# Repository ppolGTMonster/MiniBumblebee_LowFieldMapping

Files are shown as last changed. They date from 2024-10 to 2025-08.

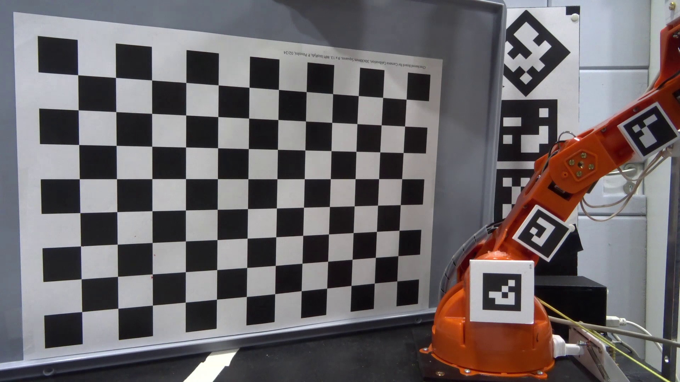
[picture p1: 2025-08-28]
4_MotionTracking/42_Software/0_calibration/calibration_result/img_calibration/image_19.jpg

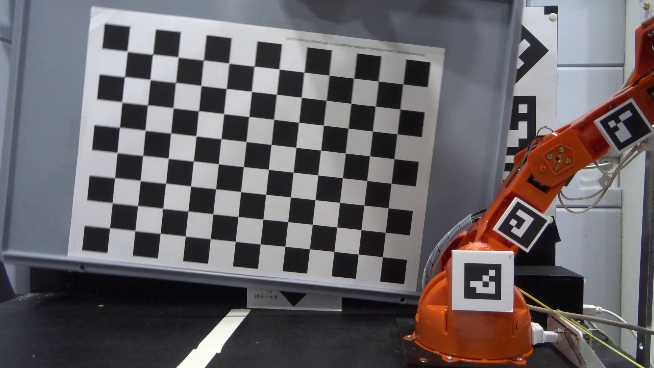
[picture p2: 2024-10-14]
4_MotionTracking/42_Software/0_calibration/calibration_result/img_calibration/image_8.jpg

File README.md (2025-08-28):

# Easy Scalable, Low-Cost Open Source Magnetic Field Detection System for Evaluating Low-Field MRI Magnets using a Motion Tracked Robot

## Author:
Pavel Povolni <pavel.povolni@tuebingen.mpg.de>

## Other Contributors to this hard- and software:
Felix Glang
  *  https://github.com/fglang
  * helped with the optimizers to design the hardware (fmincon & genetic)

Praveen Valsala
  * https://github.com/praveenivp
  * helped with reconstruction of MRI Data

Florian Birk
  * https://github.com/birkfl
  * helped with the Motion Tracking & the openCV Library

Sergej Maltsev
  * https://github.com/TheWinterProgrammer
  * helped with the Hardware 

## How to use

We tried our best to make the hardware as reproducible as possible and to develop the software without expensive extra toolboxes in Matlab (data evaluation), Python (motion tracking) and C++ (embedded code).
The PCBs were designed in KiCad 7 (free).
The mechanical components were designed with Autodesk Inventor 2021, although the Step files can be opened in any other CAD tool.

To get you started with the project as easily as possible, there are 4 instruction pdf's:
* Hallsensor (description of hardware & software for the hall sensor and calibration)
* Robot (description of the hardware & software for the robot used, including control)
* Motion tracking (description of the motion tracking setup & camera, including calibration)
* Mapping (description of the measurement process)

## Name
We always refer to this robot as Mini-Bumblebee in our team. The “big” Bumblebee refers to the large cubic robot that was built. Bumblebee itself stands for:
* B-Field
* Unterstanding and
* Mapping using
* Benchmarked
* Localized Hall
* Effect-based 
* Background
* Estimation and
* Evaluation

## Citing

If you use this code, please cite the corresponding paper:

Povolni, P., Bendfeld, R., Maltsev, S. et al. Easy scalable, low-cost open-source magnetic field detection system for evaluating low-field MRI magnets using a motion-tracked robot. Magn Reson Mater Phy (2025). https://doi.org/10.1007/s10334-025-01239-1

https://link.springer.com/article/10.1007/s10334-025-01239-1

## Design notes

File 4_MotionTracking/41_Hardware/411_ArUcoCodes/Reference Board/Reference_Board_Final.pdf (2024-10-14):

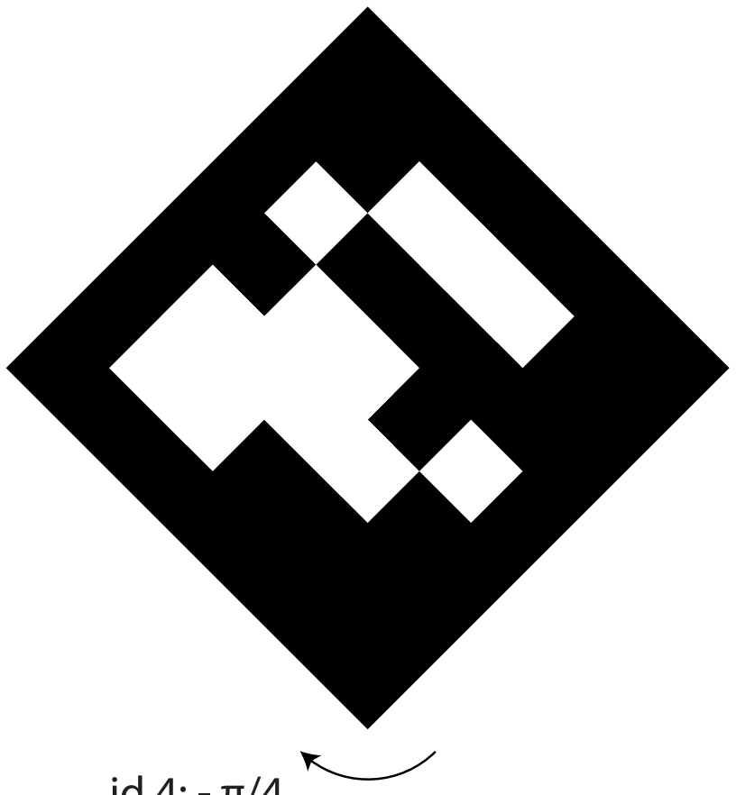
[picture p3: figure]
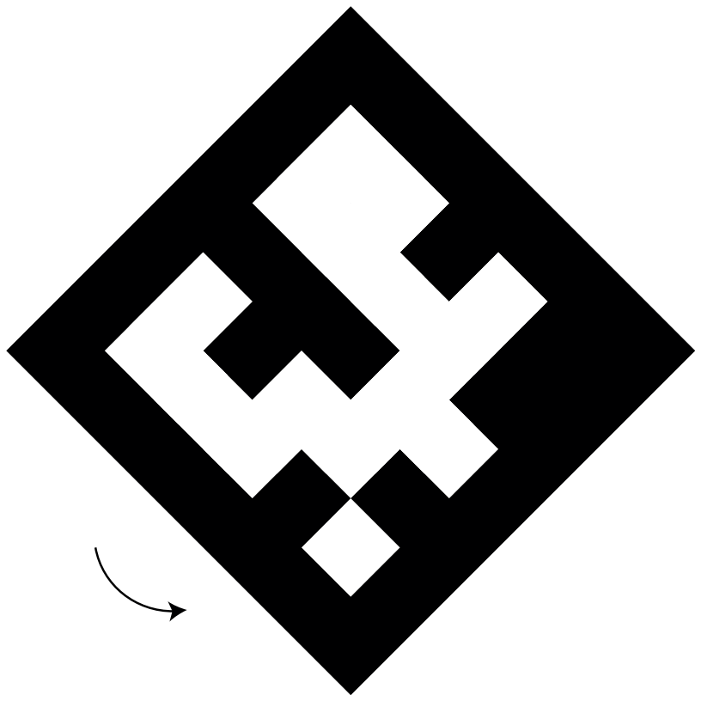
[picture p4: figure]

id 5 | id 4: - π/4 | id 3 | id 2: + π/4

id 1

id 0

# ArUco 5x5, 80x80mm

# Origin Reference Board

(0|0|0)

Translation to Magnet FOV Center: | (-181.5 |-186 | |200) mm
Translation to Robot Base Center: | (340-d |-108 | |200) mm

### d: Distance between edge of reference board and robot base holder (square with side length 130mm)

y

x
z

O RB

ID | x | y | z | Rotation
0 | 340 | 40 | 0 | 0
1 | 340 | 130 | 0 | 0
2 | 340 | 230 | 0 | + π/4
3 | 240 | 230 | 0 | 0
4 | 140 | 230 | 0 | - π/4
5 | 40 | 230 | 0 | 0
6 | 60 | -48 | 60 | + π/4

Position ArUco Center, Size ArUco: 5x5, 80mm id6: Positioned on extra 3d-printed holder
MPI bioKyb, P. Povolni, 02/24

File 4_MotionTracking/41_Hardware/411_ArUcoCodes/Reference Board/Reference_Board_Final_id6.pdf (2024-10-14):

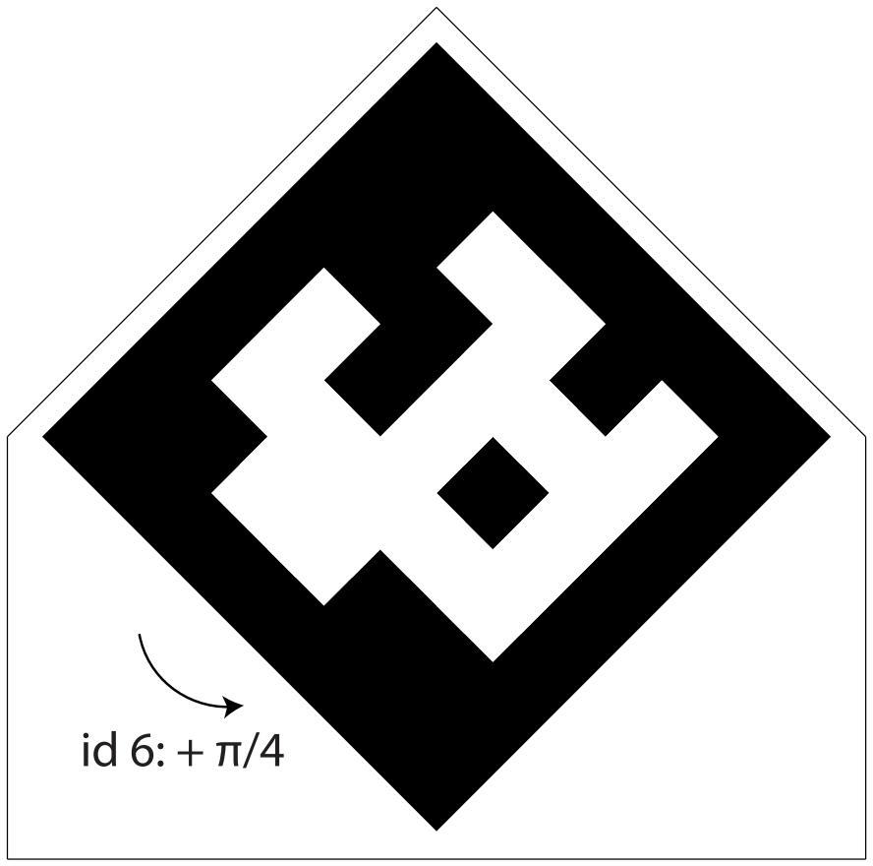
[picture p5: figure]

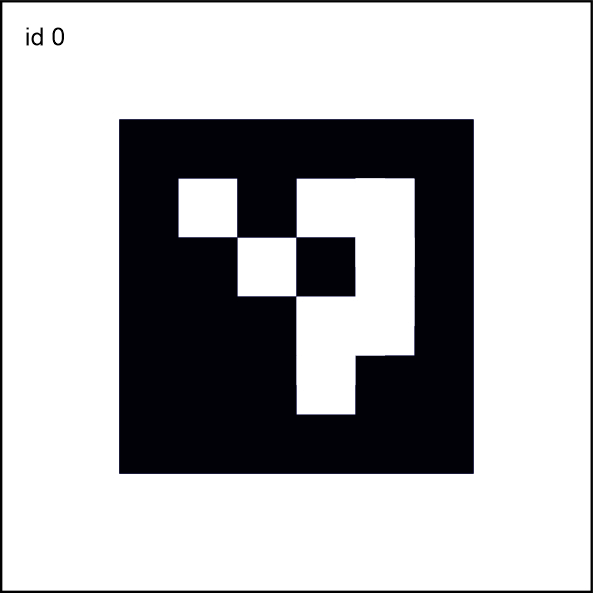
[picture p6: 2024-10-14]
3_5DoF_Robot/31_Hardware/311_RobotCAD_AutodeskInventor/2_Aruco_Marker/Marker_Robot_id0.jpg

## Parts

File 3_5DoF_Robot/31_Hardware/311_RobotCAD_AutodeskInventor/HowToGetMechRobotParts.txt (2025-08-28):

In this project, we used the TinkerCAD Braccio robot from Arduino.
CAD is not absolutely necessary. 
In our case, the robot's CAD was used to position the markers correctly and measure the lengths and positions. 

You can download the CAD for the Arduino robot directly:
https://content.arduino.cc/assets/braccio%20cad.zip

We used the CAD from GeekThomad from the GrabCAD platform:
https://grabcad.com/library/arduino-braccio-robotic-arm-1/details?folder_id=13655787
Published: April 21, 2023
(Check License: https://grabcad.com/terms, commercial use is prohibited)
This CAD is much better structured and much easier to use. Take a look and see what you need and which you can use.

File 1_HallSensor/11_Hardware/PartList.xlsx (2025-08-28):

Order list for electronic components
ID | Part-Info | Manufacturer | Part# Manufacturer | Part# Mouser | Amount | Comment
A1 | µC ESP32 Seeed XIAO Module | Seeed Studio | 113991054 | 713-113991054 | 1
C2,C4,C13,C6,C10,C26,C7,C25,C16,C20,C19,C24,C17,C22,C9,C14,C15,C12,C27,C28,C8,C21,C11,C5,C18,C23 | C 100nF | Wurth Elektronik | 885012206095 | 710-885012206095 | 26 | could be any cheaper option
C33,C34,C29,C30,C32,C35,C1,C36,C31,C3 | C 10uF | Wurth Elektronik | 885012106006 | 710-885012106006 | 10 | could be any cheaper option
J1 | Connector Hallsensor PCB (Male) | Phoenix Contact | 1844249 | 651-1844249 | 1 | could be any cheaper option. No big deal regarding shielding or similar
J1-2 | Connector Hallsensor Wire (Female) | Phoenix Contact | 1840395 | 651-1840395 | 1 | could be any cheaper option. No big deal regarding shielding or similar
J3 | Connector Power PCB (Male) | Phoenix Contact | 1844210 | 651-1844210 | 1 | not necessary (USB C has enough power)
J3-2 | Connector Power Wire (Female) | Phoenix Contact | 1840366 | 651-1840366 | 1 | not necessary (USB C has enough power)
H7,H2,H4,H5,H6,H1,H8,H3 | Hallsensor +-100mT Type | Allegro MicroSystems | ALS31300EEJASR-1000 | 250-31300EEJASR1000 | 8
H7,H2,H4,H5,H6,H1,H8,H3 | Hallsensor +-50mT Type | Allegro MicroSystems | ALS31300EEJASR-500 | 250-31300EEJASR500 | 8
D10,D13,D2,D15,D3,D5,D12,D1,D14,D9,D16,D6,D11,D7,D4,D8 | LED red, Low Power | ams OSRAM | LS L29K-G1J2-1 | 720-LSL29K-G1J2-1-Z | 18
 | R 0Ohm | Vishay / Dale | RCS06030000Z0EC | 71-RCS06030000Z0EC | 18
R1,R63,R65,R66,R44,R67,R61,R64,R62 | R 10kOhm | YAGEO | AC0603JR-0710KL | 603-AC0603JR-0710KL | 9
R17,R28,R15,R43,R30,R19 | R 11.5kOhm | Bourns | CR0603-FX-1152ELF | 652-CR0603FX-1152ELF | 16
R52,R9,R48,R56,R3,R46,R50,R54,R60,R6,R2,R8,R58,R10,R4,R5 | R 147 Ohm | YAGEO | RC0603FR-13147RL | 603-RC0603FR-13147RL | 16
R42,R16,R29,R18,R31 | R 23.2kOhm | Bourns | CR0603-FX-2322ELF | 652-CR0603FX-2322ELF | 16
R7 R2 | R 2kOhm | YAGEO | AC0603FR-072KL | 603-AC0603FR-072KL | 2
R46, R61, R50, R52, R54, R56, R58, R60 | R 820 Ohm | TE Connectivity / Holsworthy | CRGCQ0603F820R | 279-CRGCQ0603F820R | 8
SW1 | Reset Push-Button | CUI Devices | TS04-66-73-BK-260-SMT | 179-TS046673BK260SMT | 1 | not necessary (Power Cycle does the same)
Mechanical Parts (Self Print etc)
Name | File Location | How to manifacture | Amount
Base_Protection | 112_CAD Files\Base | * 3D Print or * Laser Cutting or * manual (sawing/drilling) | 2
Hallsensor_DistanceBolt_8mm4 | 112_CAD Files\SensorHead | * 3D Print (PETG) | 3
Small Parts
Name | Amount
M3 15mm Plastic Screws with washer/nut | 3
Cable tie 2.5mm | 2

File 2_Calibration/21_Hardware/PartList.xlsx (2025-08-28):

Mechanical Parts (Self Print etc)
Name | File Location | How to manifacture | Amount
1) Flange
Mounting_ Ring_ Rear_Part1 | 213_CalibrationSolenoid_CAD_AutodeskInventor\Cylinder | Lasercut (5mm Plexiglas) the best, 3D Print (PETG) also possible | 1
Mounting_ Ring_ Rear_Part2 | 213_CalibrationSolenoid_CAD_AutodeskInventor\Cylinder | Lasercut (5mm Plexiglas) the best, 3D Print (PETG) also possible | 1
Mounting_ Ring_ Rear_thickening | 213_CalibrationSolenoid_CAD_AutodeskInventor\Cylinder | Lasercut (5mm Plexiglas) the best, 3D Print (PETG) also possible | 2
Mounting_Ring_Front | 213_CalibrationSolenoid_CAD_AutodeskInventor\Cylinder | Lasercut (5mm Plexiglas) the best, 3D Print (PETG) also possible | 1
Mounting_Ring_Front_Thickening | 213_CalibrationSolenoid_CAD_AutodeskInventor\Cylinder | Lasercut (5mm Plexiglas) the best, 3D Print (PETG) also possible | 2
2) Foot
Mounting_foot | 213_CalibrationSolenoid_CAD_AutodeskInventor\Cylinder | Propably Lasercut the best, but can be 3D printed too (PETG) | 4
3) Slider
Part 1 (Conn_t15) | 213_CalibrationSolenoid_CAD_AutodeskInventor\Slider | Lasercut (5mm Plexiglas) the best, 3D Print (PETG) also possible | 1
Part 2 (Conn_t60) | 213_CalibrationSolenoid_CAD_AutodeskInventor\Slider | Lasercut (5mm Plexiglas) the best, 3D Print (PETG) also possible | 1
Part 3 (Conn_t80) | 213_CalibrationSolenoid_CAD_AutodeskInventor\Slider | Lasercut (5mm Plexiglas) the best, 3D Print (PETG) also possible | 1
Part 4 (Conn_t25) | 213_CalibrationSolenoid_CAD_AutodeskInventor\Slider | Lasercut (5mm Plexiglas) the best, 3D Print (PETG) also possible | 1
Part 5 (Slider_Front) | 213_CalibrationSolenoid_CAD_AutodeskInventor\Slider | Lasercut (5mm Plexiglas) the best, 3D Print (PETG) also possible | 2
Part 6 (Slider_Angle_Distance_Holder) | 213_CalibrationSolenoid_CAD_AutodeskInventor\Slider | Lasercut (5mm Plexiglas) the best, 3D Print (PETG) also possible | 1
Part 7 (Slider_Angle) | 213_CalibrationSolenoid_CAD_AutodeskInventor\Slider | 3D Print (PETG) | 1
Part 8/9 in 3 diff Styles: * HallSensor_Holder_X-Axis * HallSensor_Holder_Y-Axis * HallSensor_Halterung_Z-Axis | 213_CalibrationSolenoid_CAD_AutodeskInventor\Slider\Hallsensor_Mounting | 3D Print (PETG) | each 1
Mechanical Parts (to Buy)
Name | File Location | Where to buy | Amount
enamelled copper wire, 1.5mm Diameter | 213_CalibrationSolenoid_CAD_AutodeskInventor\Cylinder\Cu_Coil | rs-online.com Nr: 779-0741 | 160m
Outer Cylinder Ostendorf Kunststoffe, No. 223000, KG EM Rohr SN 4 Coex DN/OD 200 x 500 mm | 213_CalibrationSolenoid_CAD_AutodeskInventor\Cylinder\KG_Tube_200mm_500mm.ipt | local building materials supplier (e.g. Hornbach/Bauhaus etc) | 1
Inner Cylinder Ostendorf Kunststoffe, No. 222000, KG EM Rohr SN 4 Coex DN/OD 160 x 500 mm | 213_CalibrationSolenoid_CAD_AutodeskInventor\Cylinder\KG_Tube_160mm_500mm.ipt | local building materials supplier (e.g. Hornbach/Bauhaus etc) | 1
2K Epoxy (any other can be used too) | Loctite EA 9466 | rs-online.com Nr: 244-2026 | as needed
Electronic Parts
Name | Description | Where to buy | Amount
Temperature Sensor | Type K Sensor glued to coil to measure the temperature using a standard Multimeter | rs-online.com Nr: 136-5868 | 1

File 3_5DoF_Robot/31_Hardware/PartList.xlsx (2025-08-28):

Mechanical Parts (Self Print etc)
Name | File Location | How to manifacture | Amount
1) Robot
Robot Basis (wooden Plate), 12mm, 130x130mm, Adapter_Plate_12mm | 311_RobotCAD_AutodeskInventor\4_ownParts | simply saw it | 1
Positioning_Robot (Align TinkerCAD Braccio Robot) | 311_RobotCAD_AutodeskInventor\4_ownParts | 3D Print (PETG) | 1
Halterung_Robot (Lever attached to Robot Base and Potentiometer) | 311_RobotCAD_AutodeskInventor\5_Potentiometer | 3D Print (PETG) | 1
Halterung_Winkel (Mounting PCB with Poti) | 311_RobotCAD_AutodeskInventor\5_Potentiometer | 3D Print (PETG) | 1
Adapter_Wrist | 311_RobotCAD_AutodeskInventor\3_Hallsensor_Holder | 3D Print (PETG) | 1
Adapter_Wrist_Hallsensor_220mm | 311_RobotCAD_AutodeskInventor\3_Hallsensor_Holder | 3D Print (PETG) | 1
2) Environment
Backside Wood, 22mm thick, 750x422mm | 313_EnvironmentCAD_AutodeskInventor | simply saw it | 1
Ground Wood, 22mm thick, 750x350mm | 313_EnvironmentCAD_AutodeskInventor | simply saw it | 1
2) Marker
Aruco_Basis_final_id0 | 311_RobotCAD_AutodeskInventor\2_Aruco_Marker | 3D Print (PETG) | 1
Aruco_Shoulder_final_id1 | 311_RobotCAD_AutodeskInventor\2_Aruco_Marker | 3D Print (PETG) | 1
Aruco_Shoulder_final_id2 | 311_RobotCAD_AutodeskInventor\2_Aruco_Marker | 3D Print (PETG) | 1
Aruco_Wrist_final_id3 | 311_RobotCAD_AutodeskInventor\2_Aruco_Marker | 3D Print (PETG) | 1
3) Electronics
Box_Driver_Bottom | 314_Robot_PowerElectronicDriverBox | 3D Print | 1
Box_Driver_Top | 314_Robot_PowerElectronicDriverBox | 3D Print | 1

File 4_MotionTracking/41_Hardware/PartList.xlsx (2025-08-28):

Mechanical Parts (Self Print etc)
Name | File Location | How to manifacture | Amount
1) Marker Reference
Mounting_ID6 | 413_Mounting_ID6_Reference | 3D Print (PETG) | 1
Mounting_ID6_Support | 413_Mounting_ID6_Reference | 3D Print (PETG) | 1

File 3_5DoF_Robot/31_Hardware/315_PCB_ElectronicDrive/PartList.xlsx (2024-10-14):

Order list for electronic components
ID | Part-Info | Manufacturer | Part# Manufacturer | Part# Mouser | Amount | Comment
A1 | Arduino Uno | Arduino | A000073 | 782-A000073 | 1 | Doesn't need to be original Uno. Any copy will work too (eg from Seeed/Adafruit…)
A1-2/1 | Pin-Header for Shield, 6pin | Preci-dip | 801-87-006-53-001101 | 437-8018700653001101 | 1
A1-2/2 | Pin-Header for Shield, 8pin | Preci-dip | 801-87-008-53-001101 | 437-8018700853001101 | 2
A1-2/3 | Pin-Header for Shield, 10pin | Preci-dip | 801-87-010-53-001101 | 437-8018701053001101 | 1
C11,C10,C8,C9,C12,C7,C18,C22,C19,C17,C23 | C 100n SMD1206 | KEMET | C1206C104M5RACTU | 80-C1206C104M5R | 11
C16,C15,C13 | C 47uF, Radial Elko | Wurth Elektronik | 860080674005 | 710-860080674005 | 6
C25,C21,C4,C6,C3,C1,C2,C5 | C 1uF SMD1206 | KEMET | C1206C105K4RAC | 80-C1206C105K4RAC | 8
D1 | LED 3mm | Wurth Elektronik | 151031VS06000 | 710-151031VS06000 | 3
D2 | Rectifiers 50V 1.5a S2A | onsemi / Fairchild | S2A | 512-S2A | 1
F4,F3,F2, F1 | Resettable Fuses - PPTC 6V 1.1A-HD 40A MAX | Bourns | MF-MSMF110-2 | 652-MF-MSMF110-2 | 4
F7,F6,F5 | Resettable Fuses - PPTC 13.2V .75A-HD 100A MAX | Bourns | MF-MSMF075-2 | 652-MF-MSMF075-2 | 3
J1 | Connector Power PCB (Male) | Phoenix Contact | 1803277 | 651-1803277 | 2
J1-2 | Connector Power Wire (Female) |  | 1803578 | 651-1803578 | 2
J3 | Connector Base PCB (Male) | Phoenix Contact | 1803280 | 651-1803280 | 1
J3/J4-2 | Connector Sensor Wire (Female) | Phoenix Contact | 1803581 | 651-1803581 | 2
J4 | Connector Sensor PCB (Male) | Phoenix Contact | 1803439 | 651-1803439 | 1
M3,M5,M2,M4,M6,M1 | Conenctor Stepper Motors | Molex | 22-27-2031 | 538-22-27-2031 | 6 | This connector fits exactly to the wiring of the robot used (Tinkercad Braccio Arduino).Any other connector with 2.54mm pin width (e.g. pin header) can be used
Q1 | BJT npn BC548A | Diotec Semiconductor | BC548A | 637-BC548A | 1
R1 | R 147Ohm , Precise, E196 | Panasonic | ERA-8AEB1470V | 667-ERA-8AEB1470V | 1
R10 | Relay, 10A, 5V Coil | Amphenol Anytek | AHQSH105LM100G | 523-AHQSH105LM100G | 1
R2 | R 1210 Ohm , Precise, E196 | Panasonic | ERA-8AEB1211V | 667-ERA-8AEB1211V | 1
R4,R3,R5 | R 2370 Ohm , Precise, E196 | Panasonic | ERA-8AEB2371V | 667-ERA-8AEB2371V | 3
R8 | R 1 kOhm | YAGEO | RC1206FR-101KL | 603-RC1206FR-101KL | 1
R9,R7,R6 | R 147 Ohm | KOA Speer | RK73H2BTTD1470F | 660-RK73H2BTTD1470F | 3
RV1 | Sliding potentiometer | Bourns | PTA6043-2015DPB103 | 652-PTA60432015DPB10 | 1
SW1 | Reset Push Button | CUI Devices | TS04-66-73-BK-260-SMT | 179-TS046673BK260SMT | 1
U1 | OpAmp TI LM358 | Texas Instruments | LM358P | 595-LM358P | 1
U2 | Voltage References TL431C | onsemi | TL431CLPRPG | 863-TL431CLPRPG | 1
VR1 | Linear Voltage Regulators 5V 500mA Positive 7805 | onsemi | MC78M05CTG | 863-MC78M05CTG | 1

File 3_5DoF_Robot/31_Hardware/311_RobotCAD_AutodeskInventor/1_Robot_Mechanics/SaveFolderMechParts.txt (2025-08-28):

Mechanical Parts of Robot can be saved here. Depends where you grab them

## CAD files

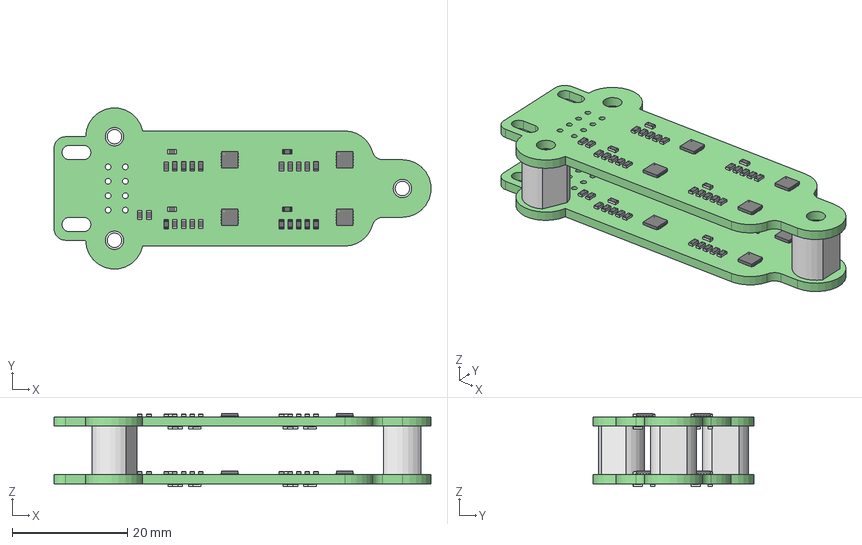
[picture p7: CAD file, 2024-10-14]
1_HallSensor/11_Hardware/112_CAD Files/SensorHead/SensorHead_ASM.stp
65.5 x 28.0 x 12.8 mm
HallSensor_Abstand_8mm4 x 3
Hallmesssonde_Verei x 2

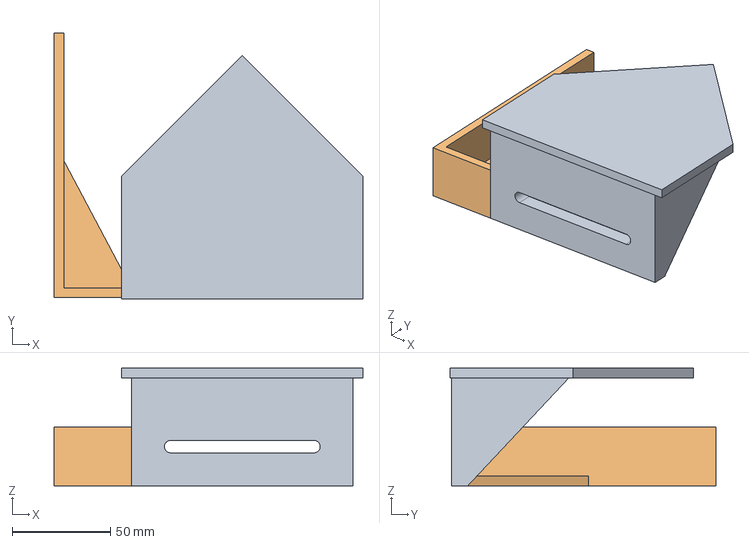
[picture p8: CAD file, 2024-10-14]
4_MotionTracking/41_Hardware/413_Mounting_ID6_Reference/Mounting_ID6_ASM.stp
157.6 x 135.6 x 60.0 mm
Halterung_ID6
Mounting_ID6_Support

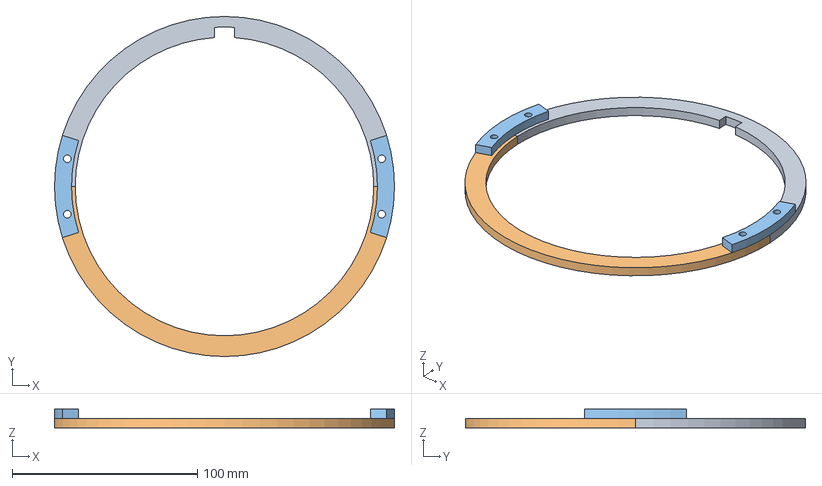
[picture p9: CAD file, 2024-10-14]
2_Calibration/21_Hardware/214_CalibrationSolenoid_CAD_STEP/Cylinder/ASM_Mounting_Ring_Rear.stp
183.6 x 183.6 x 10.0 mm
Montage_Ring_Hinten_Teil1
Montage_Ring_Hinten_Teil1_1
Montage_Ring_Hinten_Aufdickung
Montage_Ring_Hinten_Aufdickung_MIR

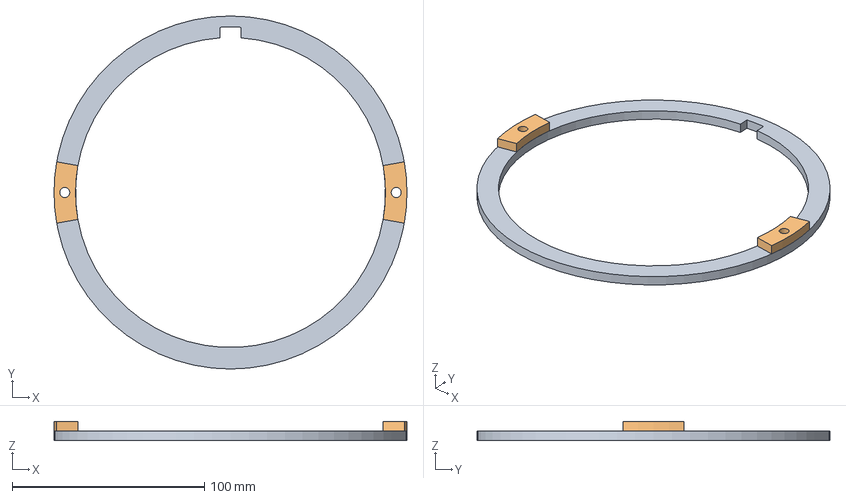
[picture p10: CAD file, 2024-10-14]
2_Calibration/21_Hardware/214_CalibrationSolenoid_CAD_STEP/Cylinder/ASM_Mounting_Ring_Front.stp
183.6 x 183.6 x 10.0 mm
Montage_Ring_Vorne
Montage_Ring_Vorne_Aufdickung_Gewinde
Montage_Ring_Vorne_Aufdickung_Gewinde_MIR

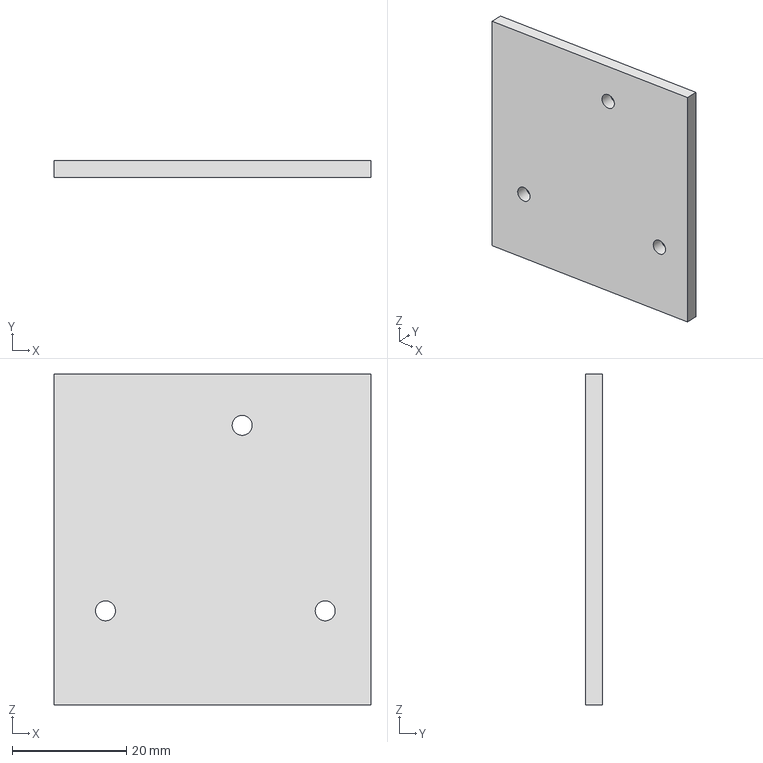
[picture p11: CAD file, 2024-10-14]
1_HallSensor/11_Hardware/112_CAD Files/Base/Base_Protection.stp
55.5 x 3.00 x 58.0 mm

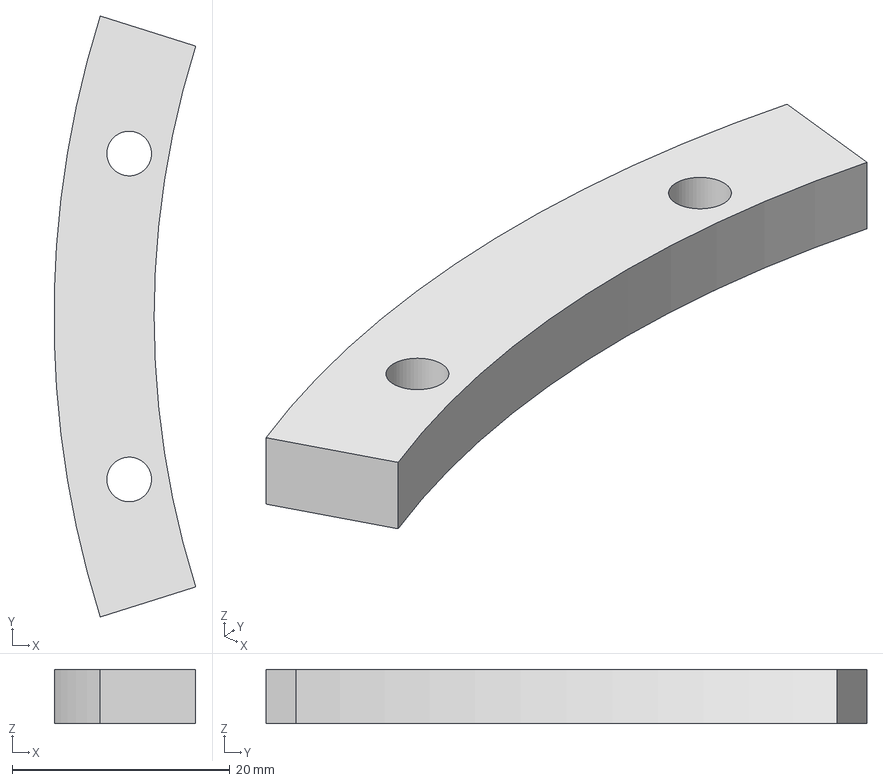
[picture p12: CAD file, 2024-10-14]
2_Calibration/21_Hardware/214_CalibrationSolenoid_CAD_STEP/Cylinder/Mounting_ Ring_ Rear_thickening_MIR.stp
13.0 x 55.2 x 5.00 mm

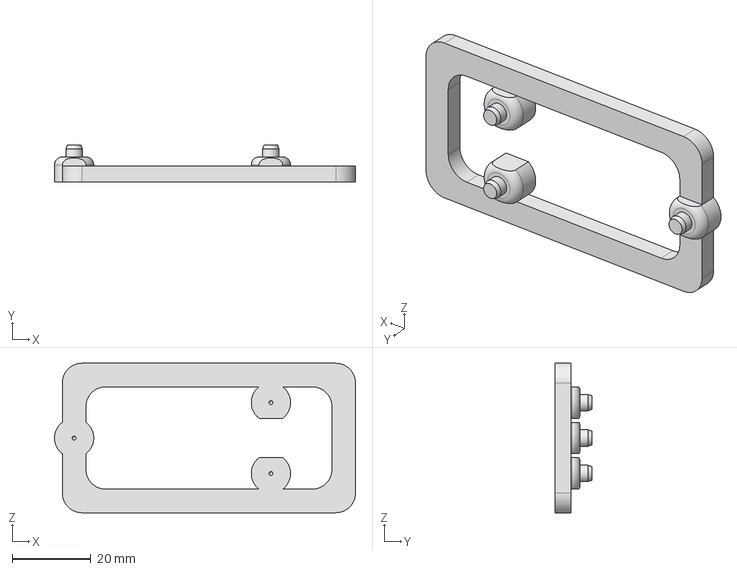
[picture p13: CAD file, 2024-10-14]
2_Calibration/21_Hardware/214_CalibrationSolenoid_CAD_STEP/Slider/Hallsensor_Mounting/Holder_Cal_UpperSensor.stp
76.5 x 9.35 x 38.0 mm

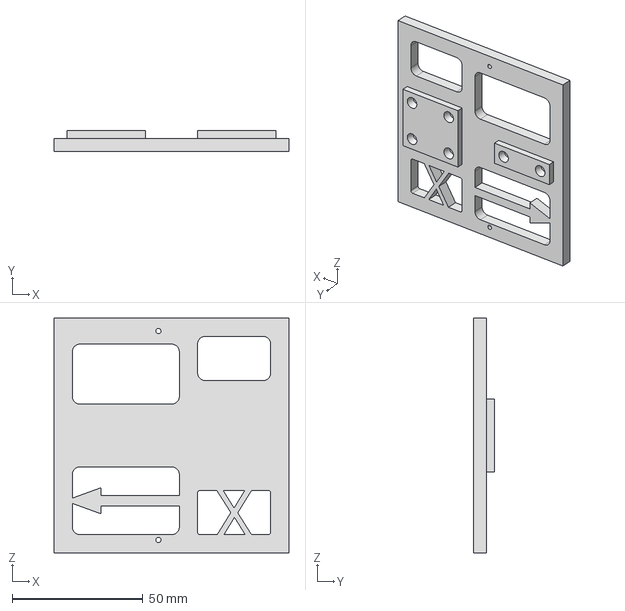
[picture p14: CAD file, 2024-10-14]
2_Calibration/21_Hardware/214_CalibrationSolenoid_CAD_STEP/Slider/Hallsensor_Mounting/X-Axis/HallSensor_Holder_X-Axis.stp
90.0 x 8.00 x 90.0 mm

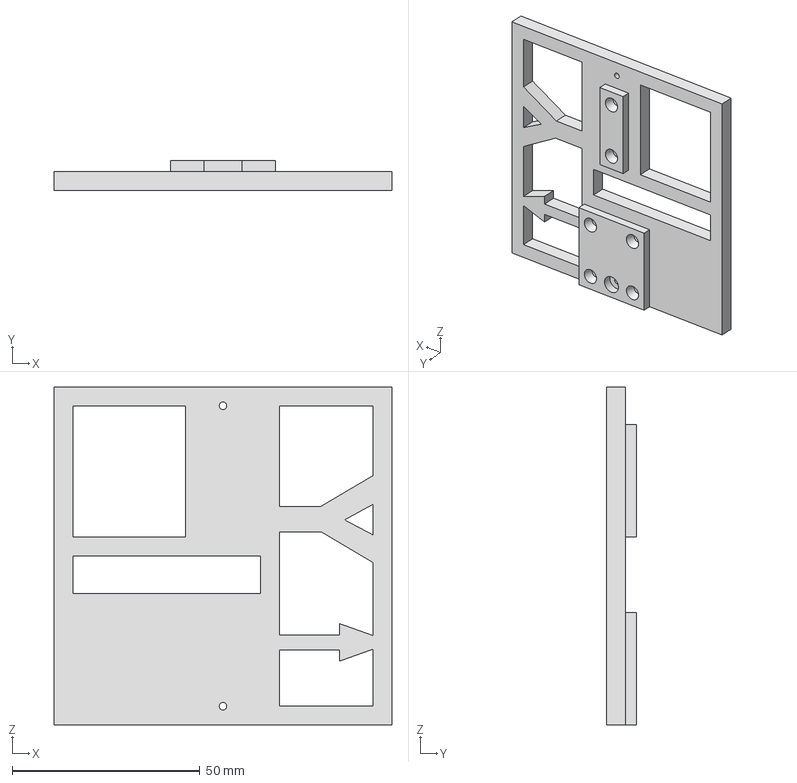
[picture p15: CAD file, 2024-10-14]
2_Calibration/21_Hardware/214_CalibrationSolenoid_CAD_STEP/Slider/Hallsensor_Mounting/Y-Axis/HallSensor_Holder_Y-Axis.stp
90.0 x 8.00 x 90.0 mm

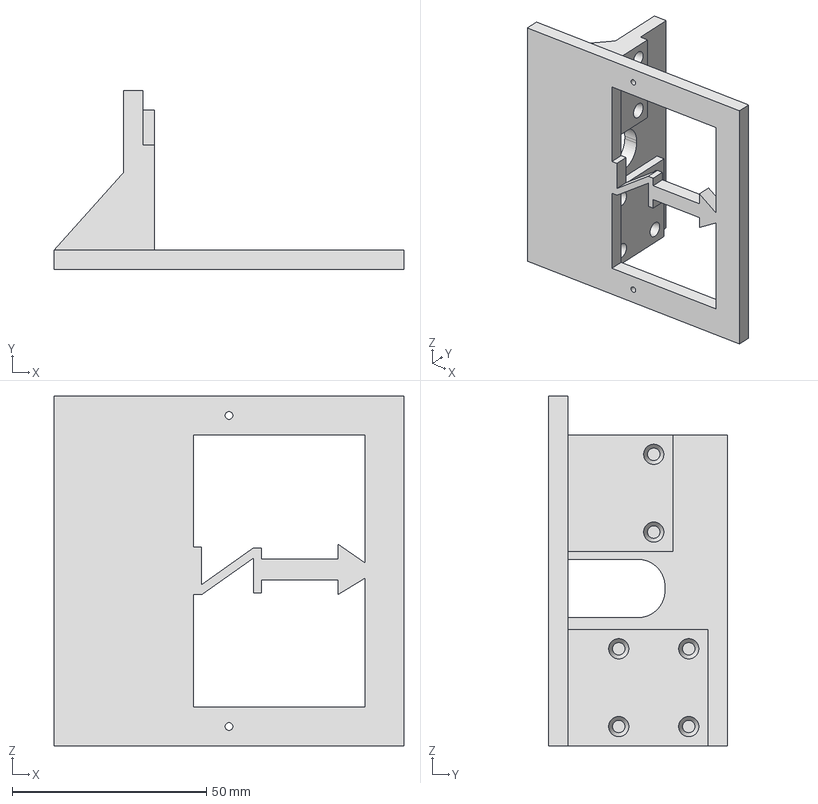
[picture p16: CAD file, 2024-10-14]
2_Calibration/21_Hardware/214_CalibrationSolenoid_CAD_STEP/Slider/Hallsensor_Mounting/Z-Axis/HallSensor_Halterung_Z-Axis.stp
90.0 x 46.1 x 90.0 mm

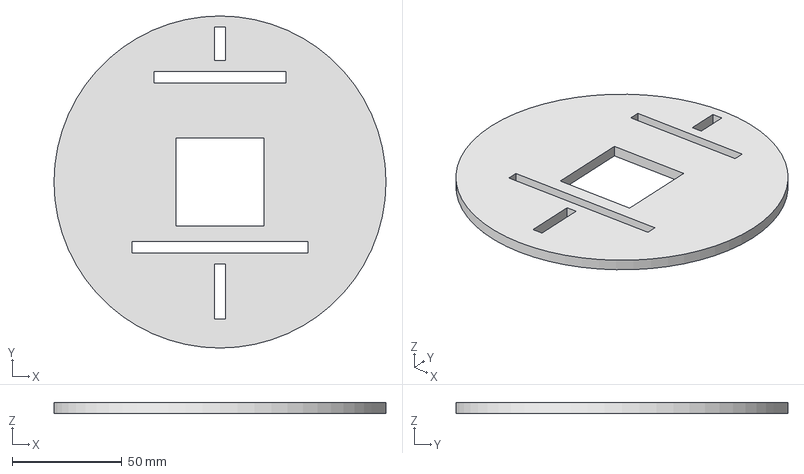
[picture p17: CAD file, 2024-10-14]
2_Calibration/21_Hardware/214_CalibrationSolenoid_CAD_STEP/Slider/Slider_Front.stp
151.0 x 151.0 x 5.00 mm

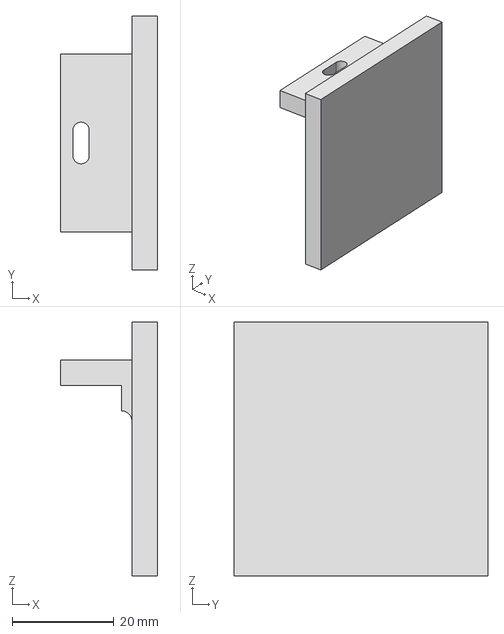
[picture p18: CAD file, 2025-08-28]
3_5DoF_Robot/31_Hardware/311_RobotCAD_AutodeskInventor/2_Aruco_Marker/Aruco_Wrist_final_id3.stp
19.0 x 50.0 x 50.0 mm

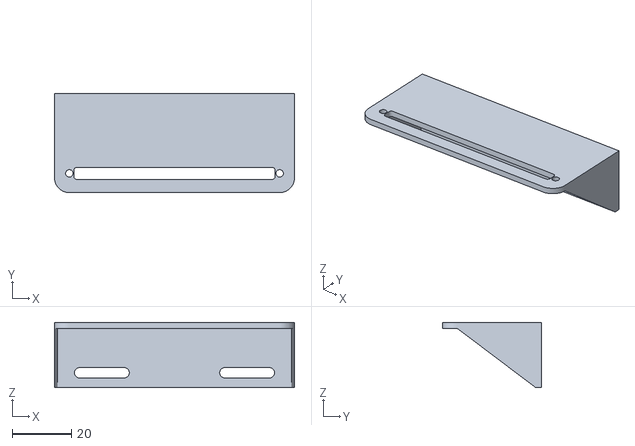
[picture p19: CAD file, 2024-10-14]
3_5DoF_Robot/31_Hardware/311_RobotCAD_AutodeskInventor/5_Potentiometer/Halterung_Winkel.stl
81.0 x 33.5 x 22.0

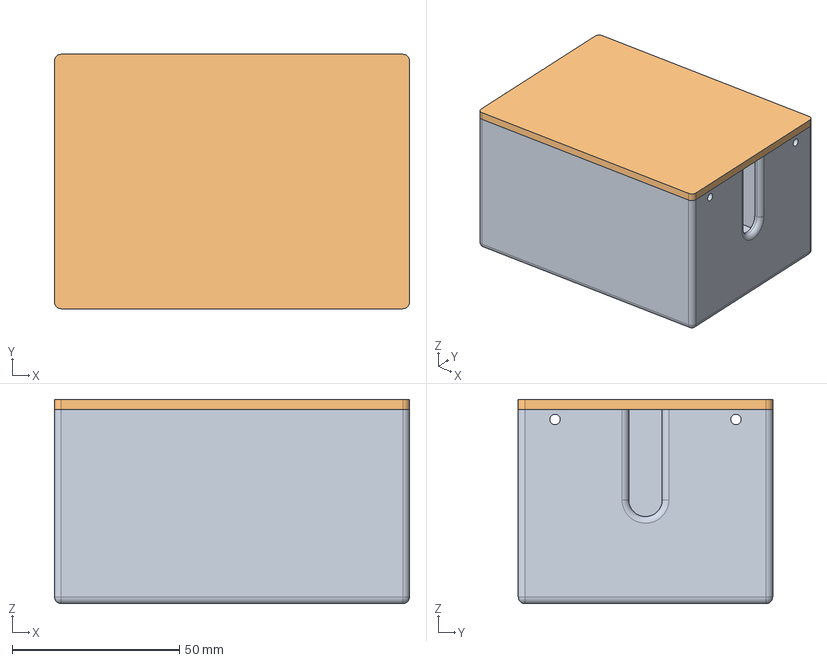
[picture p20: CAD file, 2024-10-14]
3_5DoF_Robot/31_Hardware/314_Robot_PowerElectronicDriverBox/Box_Driver.stp
106.0 x 76.0 x 61.0 mm
Box_Arduino_Unten
Box_Arduino_Oben_2

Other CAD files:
2_Calibration/21_Hardware/214_CalibrationSolenoid_CAD_STEP/Cylinder/KG_Tube_160mm_500mm.stp
2_Calibration/21_Hardware/214_CalibrationSolenoid_CAD_STEP/Slider/Hallsensor_Mounting/Holder_Cal_LowerSensor.stp
3_5DoF_Robot/31_Hardware/311_RobotCAD_AutodeskInventor/2_Aruco_Marker/Aruco_Shoulder_final_id1.stp
3_5DoF_Robot/31_Hardware/311_RobotCAD_AutodeskInventor/5_Potentiometer/Bourns_Poti.STEP
1_HallSensor/11_Hardware/112_CAD Files/Base/Base_Protection.ipt
1_HallSensor/11_Hardware/112_CAD Files/SensorHead/Hallsensor_DistanceBolt_8mm4.ipt
1_HallSensor/11_Hardware/112_CAD Files/SensorHead/Hallsensor_DistanceBolt_8mm4.stp
1_HallSensor/11_Hardware/112_CAD Files/SensorHead/OldVersions/SensorHead_ASM.0003.iam
1_HallSensor/11_Hardware/112_CAD Files/SensorHead/SensorHead_ASM.iam
1_HallSensor/11_Hardware/112_CAD Files/SensorHead/SensorHead_PCB_Single.ipt
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

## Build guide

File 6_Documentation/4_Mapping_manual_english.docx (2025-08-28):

Instructions to setting up the

Mapping of B-Field

Project

Easy Scalable, Low-Cost Open Source Magnetic Field Detection System for Evaluating Low-Field MRI Magnets using a Motion Tracked Robot

Pavel Povolni

October 2024

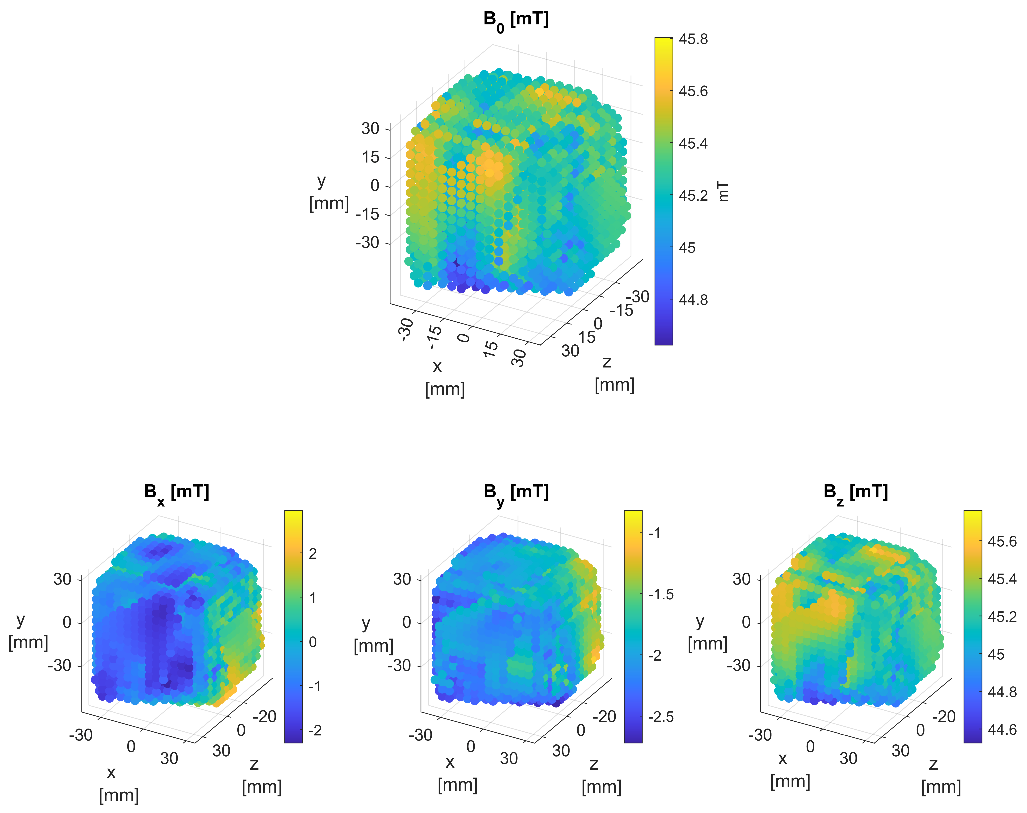
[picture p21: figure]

# 1 Preamble

These instructions describe the Mapping of the magnetic field.

Further information can be found in the publication, as well as in the Appendix and Supplementary Information referenced there.

Software used:

1. Mapping: Matlab 2021b (w/o expensive toolboxes)

If you have any further questions, please contact us!

# 2 Measurement

You can find all scripts in the folder:

...\5_Mapping

## 2.1 Preparation

Before the measurement can start, a few preparation steps are necessary. An overview is given below.

### 2.1.1 Update SetUp File

All parameters that may need to be adapted to your setup and your robot are saved and commented in the file “\ Constants_Mechanical_Robot\get_SetFile.m”.

Originally, this was supposed to be a JSON file that can also be read by the Python scripts (so that some of the values don't have to be copied/pasted). Well... at some point we forgot about that :D

Therefore, it is still partially duplicated here and you have to make sure that the values are the same in both cases.

Depending on how much you have changed in your setup, you will have to adjust the parameters significantly. If you have set it up the same way, you should have to only make little or no changes.

The following is an overview of all parameters:

1. Mechanical Constants
- Mechanics of the robot (length of the individual links and joints)
- Definition of the internal distances on the Sensor Head (distance to each other). The point "P5" defines the front screw-on point (see Figure 1), center of the screw, underside of the lower PCB
- Definition of the translation of the robot base and the magnet (center of the FOV) to the origin of the Reference Coordinate System (ORB)
2. Kinematics
- Definition of the possible angles (in °) with the limits set in a way, that it is not possible to drive in the mechanical limit. Ss well as offset values (definition of the zero angle differs in Motion Tracking and in robot control)
- Horizontality (tol_horizontality)

Due to the kinematics, the sensor cannot be moved to every point while it is positioned perfectly horizontally. This parameter specifies how large the angular deviation from the horizon may be.

- Definition of the mechanical robot tolerances:

Due to tolerances in the assembly of the robot done by us (in particular the mechanical mounting of the motors), there are differences between the angles set in the control system and the angles actually approached. We have determined this tolerance as follows: The arm should be completely vertical upwards and the base should be oriented in the direction of the magnet. To do this, we send the robot controller the following angles in a serial command window: “+090, +090,+090,+090”.

These angles are changed iteratively until the arm reaches the desired position. In our case, for example, the robot is aligned towards the magnet with a base angle of 85° (instead of the ideal 90°). The offset for the base is then calculated as: 90-85

3. Communication Setup
- Specify the serial ports that you have assigned to the Hall sensor and the robot controller (resp. which are assigned by your operating system)
4. Setup for Camera Based Measurement
- Specify the recording limit of your camera.
- Duration of how long the robot wait at a position (here 16s) and how long the robot has time to move to this position (4s)

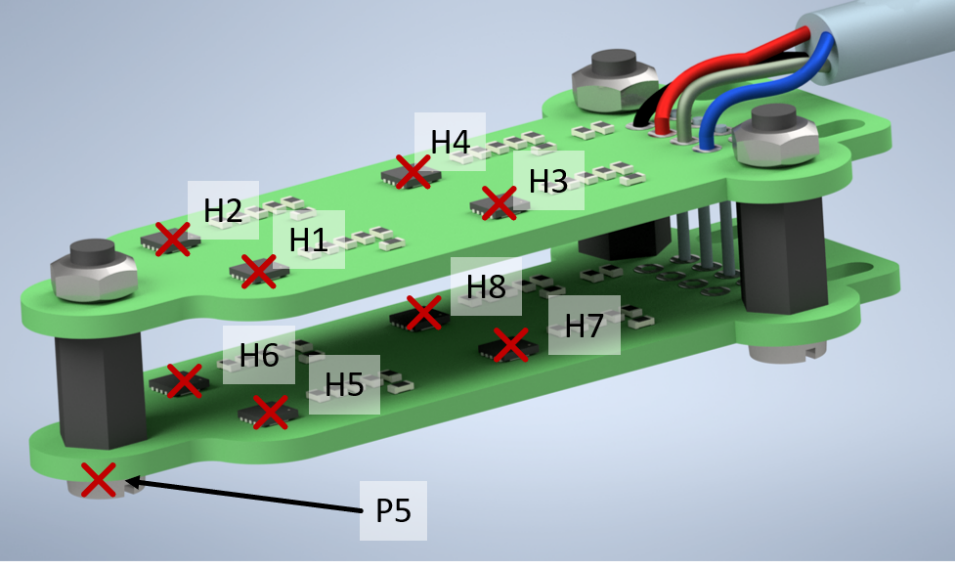
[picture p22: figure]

Figure 1: Position of Hall Sensors and Point "P5" on the Sensor Head

### 2.1.2 Generate Kinematics, FOV & Trajectory

Before the measurement, the points of the FOV to be approached and the resulting robot angles are calculated using inverse kinematics.

The inverse kinematics is underdefined (since we have 3 position coordinates, but are calculating 4 angles). The problem is optimized (using fmincon), considering the permitted horizontality.

Use this (commented) script for the calculation:

“\Generate_Kinematics_and_FOV\ Generate_Trajectory_FOV_Coordinates.m”

At the moment only cubic FOVs are calculated. If you want to calculate other FOVs (e.g. spiral, or cylindrical) you have to adapt the script (probably only the function Function_TrajectoryFOV_GenerateCube.m is enough, but check if the rest works).

The 2 main parameters that you should adjust are:

- cube_StepSize: Specification of the isotropic step size with which the FOV is scanned. For the maximum benefit of the 8Channel Hall sensors, common divisors/multiples of the Hall sensor distances should be used, which are predefined as 5,10,20,40mm. The script checks whether your selected steps size is part of this list and adjusts it if necessary.
- cube_FOVSize: Size of the FOV that is to be mapped. Specification of the x/y/z size as a vector. Uses a multiple of the StepSize so that the 8 Hall sensors distributed on the Sensor Head are used to maximum effect (and the measurement therefore has the maximum speed)

A step size of 5mm is ideal for precise Mapping. For gradient mapping and for tests, larger step sizes are useful (in our case 10mm). The FOV is such generated that the FOV center equals the center of the magnet (defined in the SetFile, see 2.1.1).

The calculated FOV is then used to calculate the joint angles to be set for the robot and to calculate the trajectory. The trajectory is simulated and displayed in a plot (good for debugging, see Figure 2). However, this simulation takes a certain amount of time. You can deactivate the plots with the "plot_flag" flag.

The points reached by the robot are not necessarily identical to the desired position. This is due to the limiting kinematics, the desired horizontality of the sensor and the control of the robot (only whole angles can be set).

The calculated angles are saved in the following file and imported again later in the Mapping:

\Save_Folder\FOV_Trajectory_alphas.mat

The trajectory (sequence of FOV points) is calculated in such a way that the robot moves as little as possible from point to point. We have found that this reduces the positioning error. Pay attention to this if you create your own FOV geometries.

The FOV is passed in yz-planes in positive x-direction.

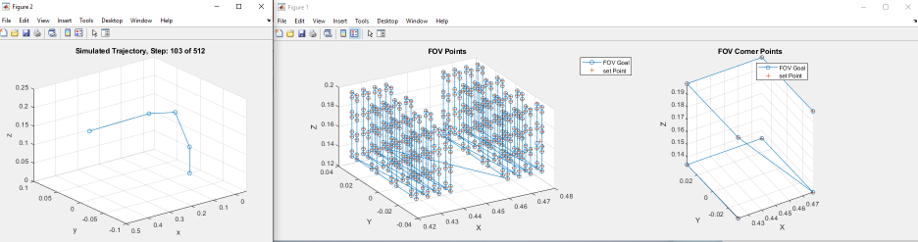
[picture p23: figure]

Figure 2: Plots of the FOV generation and calculation of the trajectory

### 2.1.3 In Case Gradient Mapping: Prepare Current Measurement

To be able to map gradients with this setup, strong fields are required (i.e. high currents and losses) to avoid resolution limit of the Hall sensors.

For current measurement, we have reused the setup from chapter 4 / 1_Hallsensor_manual. The manually switched relay there (and thus the flowing current) has been automated here.

An Arduino-Uno (script in folder “\Functions_Gradient\Code_CurrentSwitchOn”) is connected serially (9600Bd) and switches on the current (by switching the relay) as required. In our case, the wiring between the Arduino and the relay was “flying” and not rigid (a wire was connected directly to the pin header & the corresponding pin). There is therefore no PCB for this. The overall structure is shown schematically in Figure 3.

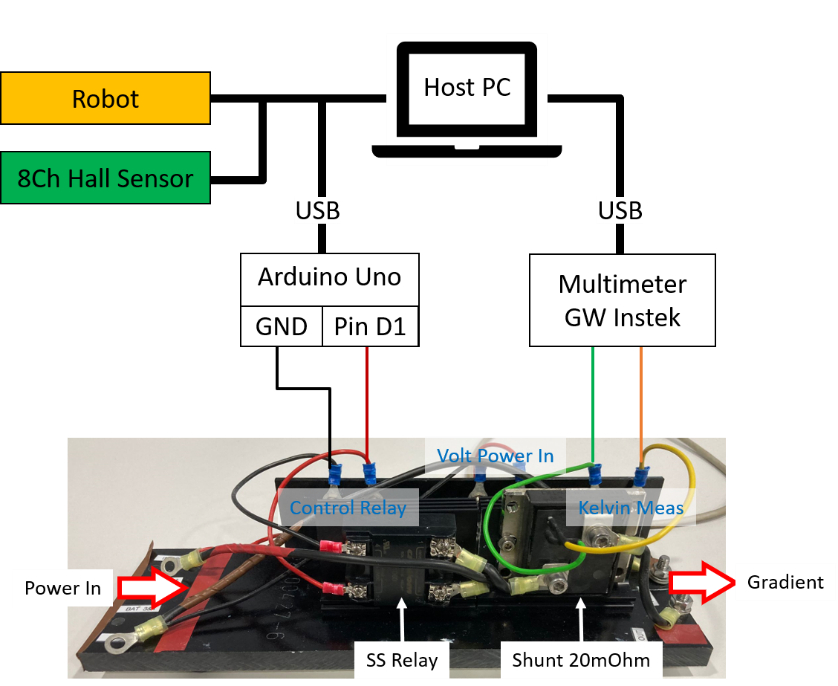
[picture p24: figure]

Figure 3: Schematic structure of the current control for gradient mapping

### 2.1.4 Move Sensor Head inside the FOV

“Chapter4/2_Robot_manual” has already described that the Hall sensor needs to be moved manually to the center of the magnet at the start of the Mapping. The reason for this is the complex trajectory required to move the Sensor Head into the magnet (due to the long arm on which the Hall sensor is mounted).

Pay particular attention to this, as a crash of the robot with the FOV can damage something (your DUT, the sensor or the arm itself). Unfortunately, this happened to us due to inattention. The servo motors generate an enormous amount of torque and broke the arm through (mounting of the sensor) during the crash.

## 2.2 Run Magnet Mapping

Now it’s time – the final Mapping can start!

After everything is set up and all the software is prepared… yes, that was a really long way - hang in there you're almost done!...

You start the Mapping of the magnet with the script "Main_Measurement_Halbach_Magnet.m". We have measured a Halbach, hence the script name. But of course, any other magnet can be measured too.

It takes a few seconds to establish serial communication with the Hall sensor and the robot when the script is started.

You can use the "flag_check_corner" flag to perform a collision check before the measurement. The robot moves into the corners of the generated cubic FOV and allows you to check whether the sensor will collide with something.

This could happen, for example, if the FOV has been selected too large or the desired position cannot be reached due to the kinematics.

As soon as everything is ready, the script informs about it in the command window, that the user can start the measurement.

Now start the camera recording and start the Mapping in the Command Window with "Enter".

#### Camera Control

As soon as the camera's recording limit is reached, the measurement is interrupted. The computer beeps and reports in the command window that the camera limit has been reached. Restart the camera (see Chapter 4/3_Motion_Tracking_manual) and start further Mapping with "Enter" in the command window.

#### Retension Shoulder Relief Spring

The FOV is passed yz-plane by yz-plane in the positive x-direction. After half the measurement, half the FOV has been traveled through. The x-position of the sensor is approximately at the center of the FOV.

In our setup, it was now necessary to retension the shoulder relief so that all points can be reached in the 2nd half (especially the upper FOV half with y>FOV center). The script stops for this (comment block 7.1, line 78) and informs the user.

Install the new springs or tighten the rubber band. Restart your camera recording. Press "Enter" in the command window to start the rest of the Mapping.

In a subsequent development, it would make more sense to integrate automatic retensioning (or to install a spring that has a longer linear range)

#### Data storage

All data is sorted in the struct Save_Data. After each position, this variable is saved temporarily to protect against data loss (name "Measurement_ Save_Data").

At the end of the Mapping, the variable is saved under the name: "Measurement_ datum", whereby the current date is inserted in the name

## 2.3 Run Gradient Mapping

The script "Main_Measurement_Gradient.m" is used to map a gradient where the power supply must be switched. If you have a gradient that is cooled well enough (protection against overtemperature, constant current flow), the usual Mapping (2.2) can be used. In our case, this was not possible, so the script was extended to include switching on the gradient and a current measurement.

Essentially, there is no change to the magnet Mapping. The additional devices (multimeter and Arduino for relay control) are defined directly in the "Main_Measurement_Gradient.m" script. In our case, the multimeter could also be addressed serially. This changes depending on which multimeter you use:

All communication with the multimeter is bundled in the "Function_Gradient_GetCurrent" function. Change this function so that it is suitable for your multimeter. Alternatively, you can set up your own voltage measurement (see Chapter 4.2.3/1_Hallsensor_manual). No changes to the Matlab code should then be necessary.

Before the measurement starts, change the following parameters to your setup in this script:

- Relay_COM_Port = "COM9";
- Relay_SRL_Baud = 9600;
- Multi_COM_Port = "COM10";
- Multi_SRL_Baud = 115200;
- Multi_R_Shunt = 0.02;

The gradient is switched on for 16 seconds at each measuring point. The ohmic losses increase the temperature of the gradient and the ohmic resistance rises, which changes the current flow (depending on the current source). In our setup, a laboratory power supply was used in CC mode with sufficient voltage headroom. Therefore, the current flow was stable during the 16 seconds. To increase the accuracy, 2 current measurements (before and after the magnetic field measurement) are carried out and averaged in the evaluation at the end.

You start the Mapping by starting the script. There is no difference to the magnet Mapping in Chapter 2.2. Only a cooling phase, in which the gradient is cooled by convection, has been integrated:

#### Cooldown phase

We have included a cool-down phase every 6 measurements (2 minutes). In Line 110, the current iteration is checked and the script is stopped. The user is informed via beeps and in the command window.

We had set up a fan that constantly cooled the gradient (Figure 4). The cooling phase was about 2-5 minutes. However, we could probably have carried out the entire measurement in one run with our setup, the cooling was good enough and the power supply had enough headroom.

The camera recording was stopped during this pause and only restarted shortly before the measurement was continued. Halfway through the measurement, the shoulder relief was retensioned.

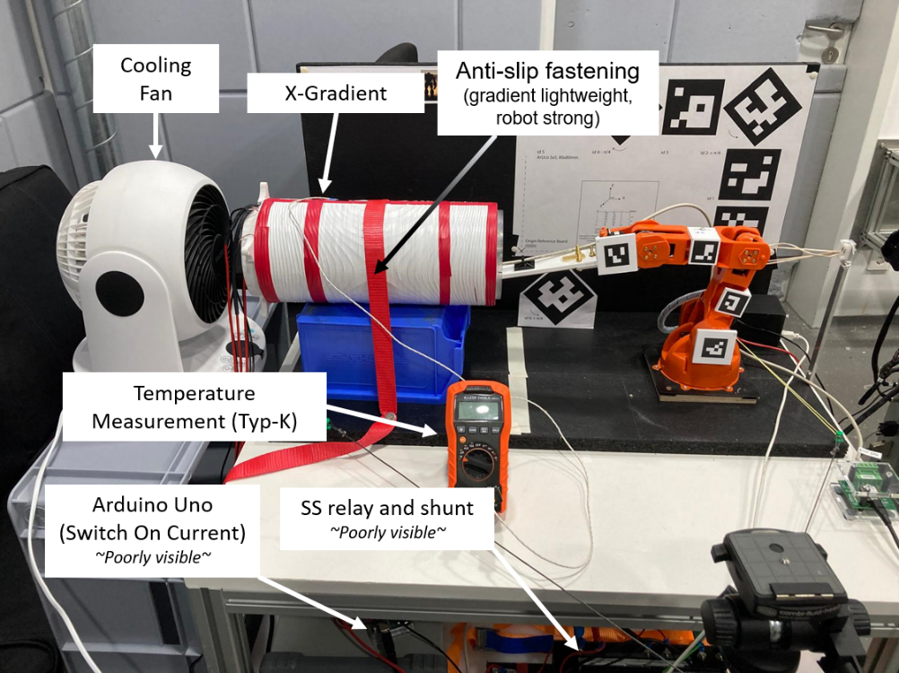
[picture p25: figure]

Figure 4: Image of the gradient measurement

# 3 Analysis in Post Processing

The measurements are complete and it's time for the evaluation. First of all, congratulations, you've come a long way and learned a lot about hardware and optical Motion Tracking!

This involves evaluating the measurement and linking the individual measurement data so that a data set is created at the end that can be used in further development steps (e.g. for calculating a shimming field).

## 3.1 Preparation

### 3.1.1 Data Handling

For the analysis you need the following 4 data collections, which are stored in the folder:

...\5_Mapping\Analysis_Mapping\Data_for_Evaluation

- Measurement data of the magnetic field from chapter 2 (this manual),

Name: "Measurement_datum.mat"

- Motion Tracking evaluation from chapter 4.2 (3_Motion_Tracking_manual),

Name: "MotionTracking_Log.csv"

- calculated (ideal) FOV from chapter 2.1.2 (this manual),

Name: "FOV_Trajectory_alphas.mat"

- Calculated calibration of the Hall sensor from chapter 4.4 (1_Hallsensor_manual),

Name: "Calibration_50mT_datum.mat"

Make sure that data from different measurements are not mixed together.

### 3.1.2 SetUp software (update parameters)

The script that is used for the evaluation is this one:

“...\5_Mapping\Analysis_Mapping\Main_PostProcessing_inclSensor.m”

In this evaluation, the "SetFile" (“get_SetFile”) is used again, which was already used in Chapter 2.1.1 has already been adapted to your system.

The entire script is heavily commented in case you want to customize anything. This script should actually work with any robot and system as long as the data looks the same. All relevant setup parameters are stored centrally in the setup file.

At this point, only a few parameters/flags remain that you can adapt to your system. These are summarized in the "%% 1) User Settings" block:

Flags

- show_plot: Flag indicating whether a plot of each tracked point (point P5 of the Sensor Head) should be shown. This plot can take quite a long time, so only every 10th point is shown (can be changed in Line 250)
- show_plot_HallSens: Flag indicating whether the trajectory of the Hall sensor should be shown. The trajectory of the Sensor Head is simulated. This plot is very helpful for debugging, but takes an extremely long time. Switch the flag off when you know that the analysis is working.
- use_CalFile: Flag indicating whether the calibration of the Hall sensor should be used. Can be helpful to qualify the effect of the calibration

Parameters

- active_Hallsens: Specification of how many of the installed Hall sensors are to be used (only relevant in the event that you only use 4 sensors, for example - i.e. only use one level)
- Tref: Room temperature in °C
- step_goal: Specifies the step size to which the measured magnetic field is interpolated. Due to the kinematics of the robot and the tolerance, the measured points deviate from the perfect FOV grid. The interpolation was helpful to simplify subsequent evaluations (e.g. shimming calculations).

Storage locations and file name

- file_HallData: Dataset of the measured magnetic field
- file_MT: Dataset of the evaluated Motion Tracking
- file_FOV: specified FOV points, which were measured
- file_CalHallData: Calibration data of the Hall sensors. It may be worth repeating the calibration of the Hall sensor over time. A more recent file can therefore also be used here.

Nice-To-Have parameters

The magnet is indicated in the plots. This helped us with debugging, as it was possible to see directly whether the tracked points are actually in the magnet itself (and for example not swapped axes in the Motion Tracking axes).

To do this, the inner cylinder of the magnet is drawn semi-transparently in the plot. In the local function “genFOVCylinder” (in the script “Main_PostProcessing_inclSensor.m”, Line 510) there are 2 parameters for this:

- r: Radius of the cylinder
- h: Length (height) of the cylinder

## 3.2 Run Analysis

Once everything has been set and the data has been stored correctly in the right place, the script can be executed. To do this, simply start "Main_PostProcessing_inclSensor.m".

Depending on which plot flags you have activated, the evaluation takes between a few seconds and few minutes

## 3.3 Results

The calculated results are saved in the file "Result_Analysis_datum.mat'" in the folder:

...\5_Mapping\Analysis_Mapping\ Result_Mapping

The following calculated variables are saved:

- x_vec/y_vec/z_vec

Position of each magnetic field point as a vector. In our Halbach Mapping, 512 positions were approached (times 8 sensors: 4096 magnetic field points, some points could not be measured and are NaN. NaNs are delated and not saved)

- Bx/By/Bz

Magnetic field strength in mT at each measured point as a vector. Same length as x_vec/y_vec/z_vec

- x_kin_q/y_kin_q/z_kin_q

Interpolated position grid (3D mesh grid) with the desired step size.

- Bx_kin_ip/By_kin_ip/Bz_kin_ip/B_kin_ip

Interpolated magnetic field, divided according to the coordinate axis (as 3D mesh grid).

The result is displayed (depending on the flags set) in a total of 5 plots, which are described below:

1. Base angle accuracy (Figure 5a)

The comparison between the measured base angles is shown. On the one hand, Motion Tracking is used and on the other hand the additionally installed sensor itself. In our example, the poorness of the angle measured by Motion Tracking (blue) can be seen directly, as it is extremely noisy. The measured value of the additional sensor is hardly noisy and is stable over time.

2. FOV comparison (mapped and actually measured), (Figure 5b)

Left: desired FOV with trajectory for point P5.

Right: Positions actually reached by P5. Small coordinate systems are shown (x=red, y=green, z=blue) to check whether all rotations have been carried out correctly.

3. Simulation of the Sensor Head trajectory, (Figure 5c)

The trajectory of the Sensor Head is simulated. This simulation is helpful to check whether the Motion Tracking and the calculated positions are correct and senseful.

4. 3D plot of all mapped positions and the B0 field at the position(Figure 6a)

Left: Plot of the positions of all measured magnetic field points (red dot) with magnetic field vector (blue) at the same position, and only the position of P5 (black cross)

Right: Scatter plot of the measured magnetic field |B_0 | and positions of P5 (black cross)

5. 3D plot of the interpolated B0 field (Figure 6b)

Scatter plot of the interpolated magnetic field

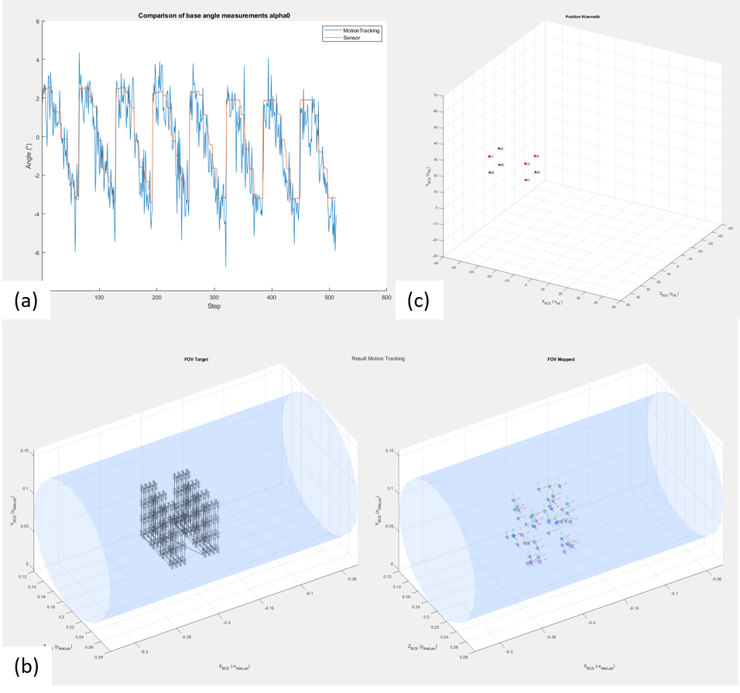
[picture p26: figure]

Figure 5: Figure 1/2/3 of the analysis

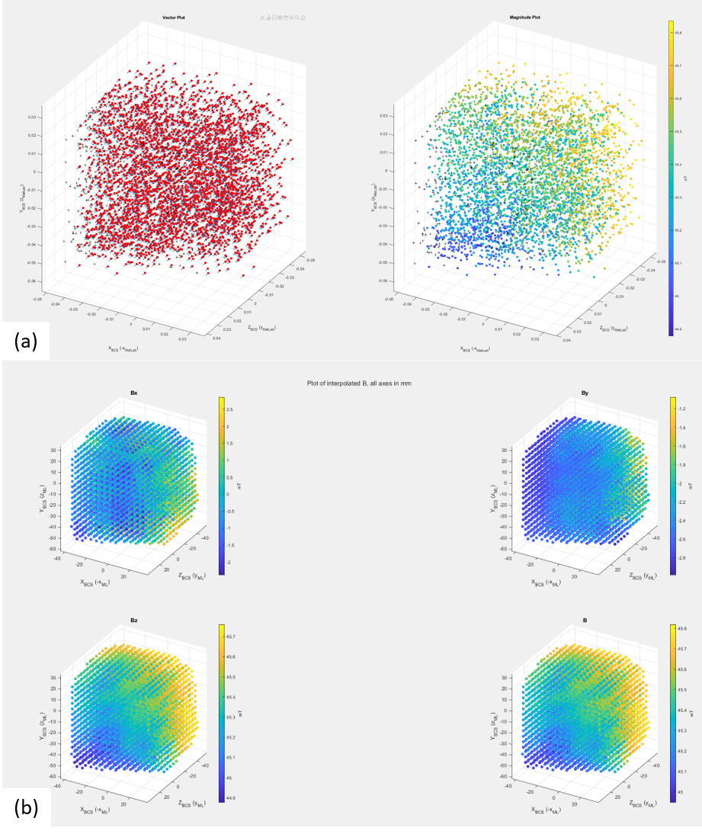
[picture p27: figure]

Figure 6: Figure 4/5 of the analysis

2 Instructions to setting up the Mapping

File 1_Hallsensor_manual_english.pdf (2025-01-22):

# Instructions to setting up the

# Hall sensor

## Project

Easy Scalable, Low-Cost Open Source Magnetic Field Detection System for Evaluating Low-Field MRI Magnets using a Motion Tracked Robot

Pavel Povolni
October 2024

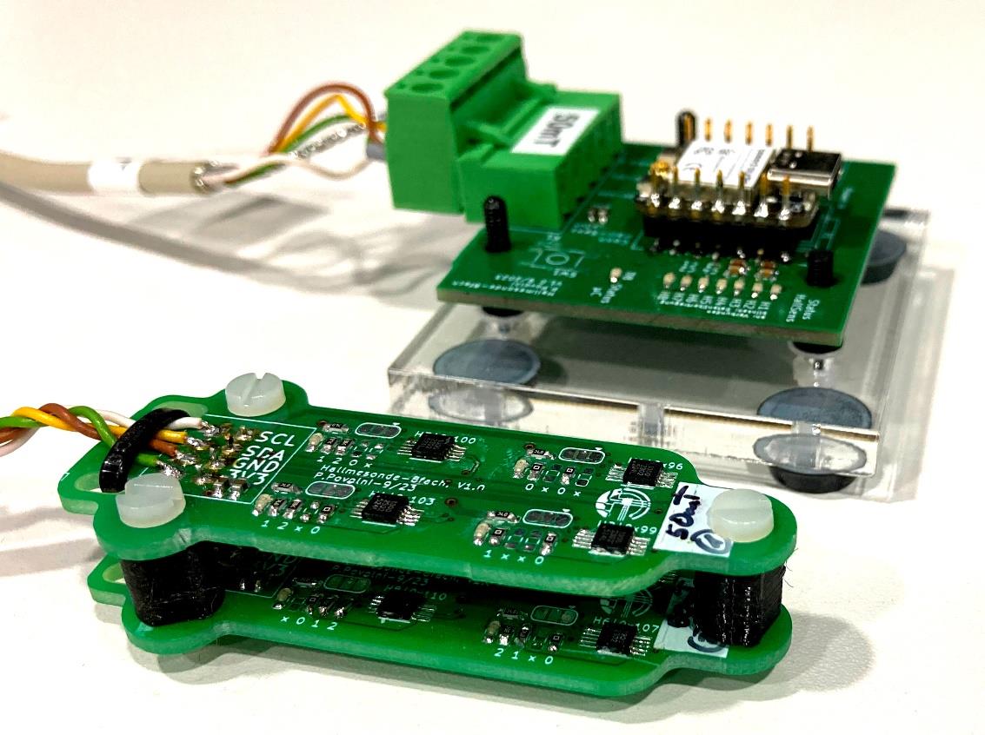
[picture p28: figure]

2
Instructions to setting up the Hall sensor

## Content

1 | Preamble | 3
2 | Hardware | 3
2.1 | Assembly PCB's | 3
2.1.1 | General | 4
2.1.2 | Addressing the IC's | 6
2.1.3 | Connectors | 6
2.2 | Mechanical Assembly | 7
2.2.1 | Sensor Head | 7
2.2.2 | Base Station | 8
3 | Embedded software (C++ code using Arduino IDE) | 8
3.1 | General | 8
3.2 | Installation ESP32 Environment | 9
3.3 | Flash | 9
4 | Calibration | 10
4.1 | Software to calculate magnetic field | 10
4.1.1 | Analytical Solution using Biot Savart | 10
4.1.2 | FEM Simulation using free Software FEMM & Python | 11
4.2 | Structure of the hardware | 11
4.2.1 | Cylinder | 12
4.2.2 | Slider | 16
4.2.3 | Current measurement and operation of the cylinder coil | 17
4.3 | Calibration Run | 20
4.3.1 | Procedure | 20
4.3.2 | Calibration Run: Linearity | 20
4.3.3 | Calibration Run: Temperature Dependence | 22
4.3.4 | Calibration Run: Static Offset | 22
4.4 | Evaluate Calibration & get Calibration Parameter | 22

3
Instructions to setting up the Hall sensor

## 1 Preamble

These instructions describe the installation, commissioning and calibration of the Hall sensor. Further information can be found in the publication, as well as in the Appendix and Supplementary Information referenced there.
Software used:
- PCB design: KiCad 7 (Free)
- Mechanical design (CAD): Autodesk Inventor 2022 (Commercial). All parts exported as .Steps
- Embedded software: Arduino IDE 2.2.1 (free)
- Calibration: Matlab 2021b (w/o expensive toolboxes), FEMM 4.2 (free)

If you have any further questions, please contact us!

## 2 Hardware

2.1 Assembly PCB's

The boards were developed in the open source software KiCad 7.0.
The design files can be found under: ...\1_HallSensor\11_Hardware\111_PCB File.
Opening the file "Hall_Probe_8Ch.kicad_pro" opens the project and allows you to edit the schematics ("Hall_Probe_8Ch.kicad_sch") and the layout ("Hall_Probe_8Ch.kicad_pcb").

The entire Hall sensor consists of 3 individual PCBs, which were connected in the layout to form a single PCB (cheaper production of the PCB itself). The boards must therefore be separated before assembling the parts.

The board is designed in 2 layers (F/B) with the following design rules:
- Minimum clearance 0.1mm
- Minimum track width 0.2mm
- Minimum via diameter 0.4mm
- Minimum residual ring 50µm
- Minimum hole 0.2mm

Our PCB was produced by the manufacturer MultiCB (www.multi-circuit-boards.eu/en). The PCB (.kicad_pcb) can be uploaded directly there. Depending on the desired quantity, the manufactured PCB costs beginning at 15€. We have also had very good experiences with the manufacturer JLCPCB (www.jlcpcb.com). There, the layout must first be converted to a Gerber file and then uploaded (https://jlcpcb.com/help/article/how-to-generate-gerber-and-drill-files-in-kicad-7)
Production is much cheaper there (6€ for 5 pieces), but you have to pay by credit card.

All necessary electronic components are listed in an Excel list: ...\1_HallSensor\11_Hardware\PartList.xlsx

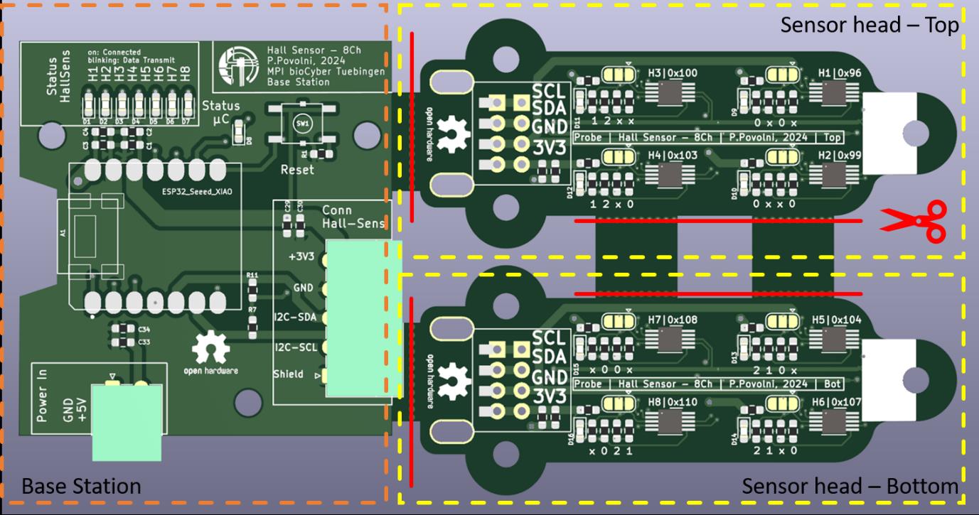
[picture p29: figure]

4
Instructions to setting up the Hall sensor

We have ordered all components from the supplier Mouser Electronics (www.mouser.com). The supplier number is also shown in the list. We have made sure that none of the components have any special (& expensive) tolerance requirements. Only the Hall sensor itself and the microcontroller must be of the specified types, so that the software will work.

2.1.1 General

- Preparation
The PCB must be sawn into individual boards before assembly. Figure 1 shows the cutting lines. A chain of via's makes it easier to break the boards off from each other. In our case, however, a fine metal saw was better and created a more controlled break. For a nice result and blunt edges, it is worth removing the remnants with a metal file.
You could also assemble the PCBs before sawing. However, great care must then be taken to ensure that no mechanical loads/vibrations act on the solder joints during sawing (otherwise they will break).

Figure 1: CAD rendering of the board (Microcontroller ESP32 is not shown)

- Soldering the Sensor Head
Both parts of the Sensor Head (top/bottom) are assembled almost identically. The only difference is the addressing of the Hall sensor ICs, which is possible via 4 resistors each (see chapter 2.1.2).
These PCBs have parts on both sides so that the head is as small as possible.

First you should solder the Hall sensor ICs. Take your time, because the footprint (DFN10) is challenging:
The pins are mainly located under the housing and a pad in the middle is used for mechanical attachment (no electrical function). For this IC, soldering with hot air and a lot of flux is recommended. The pins can also be contacted on the side. With plenty of flux and a chisel-shaped soldering tip, they can be contacted with the large pads on the PCB. A short circuit can be recognized optically with a microscope/magnifying glass. There are good tutorials on YouTube how to solder such parts.

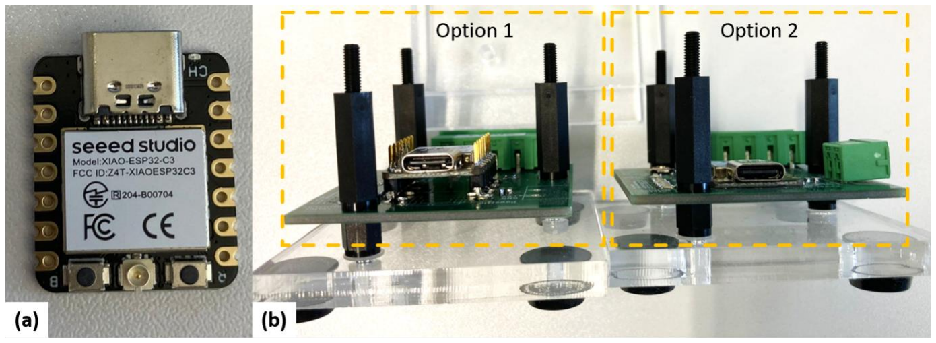
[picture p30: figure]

5
Instructions to setting up the Hall sensor

SMD footprint 0603 was used for capacitors/resistors/LEDs. With a little practice and a fine soldering tip (possibly a magnifying glass/microscope for checking), these can be soldered well. Take your time if you’re not trained & don’t worry it’s easier to solder such small parts than expected. The SMD jumpers (gold-colored footprints in Figure 1) were added to the schematic to change the "interrupt" mode of the Hall sensors if necessary. However, the interrupt was never used, so the jumpers can be removed in a future version.

- Soldering the Base Station
For the Base Station, the microcontroller (XIAO SEEED based on ESP32C3) should be soldered first. There are 2 options (see Figure 2): Either the microcontroller is soldered on directly (b, option 2) or SMD pin headers (e.g. Mouser: 855-M20-8770746 , Harwin M20-8770746) (b, option 1) are used. The pinheaders are not really necessary. But maybe it makes sense for you if the microcontroller can be replaced in a plug&play-way (then you would need to add female pin headers to the Microcontroller).

Figure 2: (a) Microcontroller used (seeed XIAO-ESP32-C3). (b) Showing the 2 options how the microcontroller can be soldered.

The button SW1 is used to reset the microcontroller. The microcontroller itself also has a reset button, so the extra button SW1 is not necessary and does not need to be assembled. If a reset was necessary, we usually did it via power cycling.

The connector J3 is intended for the 5V supply of the sensor and is parallel to the USB supply (in case the USB supply is not sufficient). However, we have always used the USB supply.

The status of the Hall sensors is displayed via LEDs D1 to D7. There are 8 sensors connected, but the microcontroller only has 7 pins left in the end. Therefore, sensors 7 and 8 share one LED.

The Hall sensors are read out via I2C. A high baud rate is therefore necessary for the fastest possible communication, which is limited by the performance of the I2C drivers in the Hall sensor and microcontroller and by the pull-up resistors R7/R11. The calculation of the pull-up resistors is explained in the schematics and can be adapted by you if you want to connect a different number of Hall sensors, for example. In our setup, 100kBaud has been successfully and reliably tested.

6
Instructions to setting up the Hall sensor

2.1.2 Addressing the IC's
The used Hall sensors can be set to 16 different I2C slave addresses by hardware (external voltage at pin Adr0 and Adr1) (see data sheet, page 22).
This external voltage is generated via two voltage dividers
R_Ad0_HS || R_Ad0_LS
&
R_Ad1_HS|| R_Ad1_LS
Hall sensor | I2C address | Ad1 | Ad0
U | R_HS | R_LS | U | R_HS | R_LS
H1 | 0x96 | 0 V | nc | 0 | 0 V | nc | 0
H2 | 0x99 | 0 V | nc | 0 | 3.3 V | 0 | nc
H3 | 0x100 | 1 V | 23.2k | 11.5k | 0 V | nc | 0
H4 | 0x103 | 1 V | 23.2k | 11.5k | 3.3 V | 0 | nc
H5 | 0x104 | 2.2 V | 11.5k | 23.2k | 0 V | nc | 0
H6 | 0x107 | 2.2 V | 11.5k | 23.2k | 3.3 V | 0 | nc
H7 | 0x108 | 3.3 V | 0 | nc | 0 V | nc | 0
H8 | 0x110 | 3.3 V | 0 | nc | 2.2 V | 11.5k | 23.2k
nc = not connected/open

To simplify the PCB assembly, the necessary resistors are encoded on the layout:
- x: Not connected/open
- 0: 0 Ohm
- 1: 11.5 kOhm
- 2: 23.2 kOhm

2.1.3 Connectors
Phoenix Contact Pluggable Terminal Blocks are installed on the Base Station (see part list). The advantage of these plugs are the screw able connections to the cable, so that no expensive crimping tools are required. Any other plug connection is also possible and can be adapted by you according to your wishes (and also available tools in your lab). One pin of the sensor connector (J1) is intended for connecting the cable shield (reduction of EMC). The shield must not (!) be connected to GND on the Sensor Head (preventing ground loops)!

Typically, pins of connectors are nickel-plated (and therefore ferromagnetic). The cable is therefore soldered directly to the Sensor Head and strain-relieved with a cable tie (see details in Fehler! V erweisquelle konnte nicht gefunden werden.).

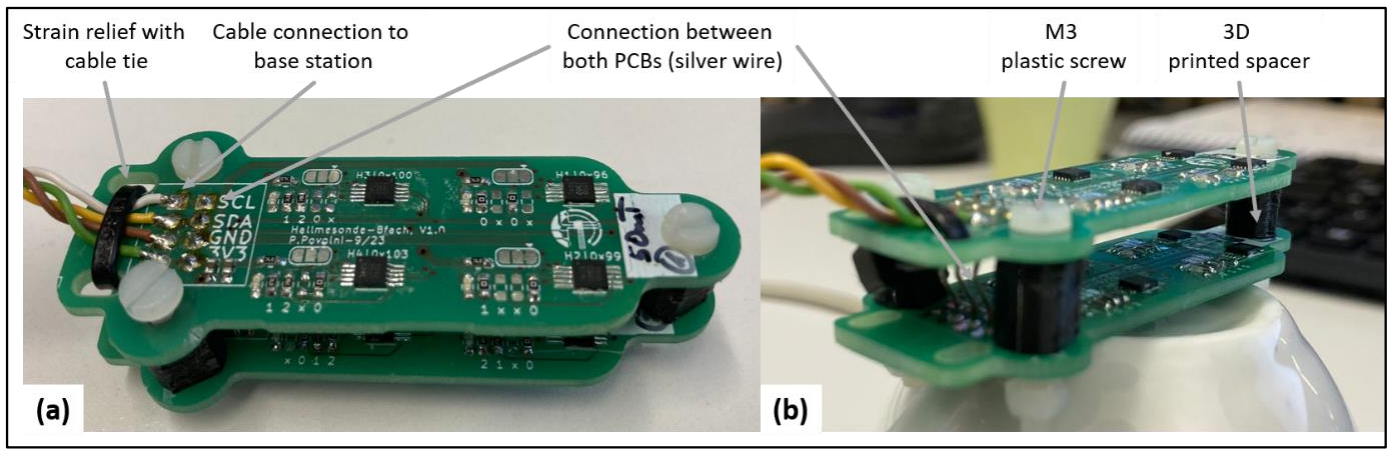
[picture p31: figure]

7
Instructions to setting up the Hall sensor

2.2 Mechanical Assembly

2.2.1 Sensor Head
After both PCBs of the Sensor Head have been soldered, they should be electrically tested (the solder joints of the Hall sensor IC caused us problems until they worked perfectly). To do this, connect each board directly to the Base Station and test them one after the other (the software recognizes when a sensor is not accessible - in this case the sensors on the other board - and skips the value).

The assembled sensor is shown in Figure 3 is shown.
The connecting cable is soldered on directly. We have used a shielded cable with a length of 90 cm (so that the Base Station is outside the magnetic field). A longer cable is also possible. However, in case of longer cables, the baud rate of the communication may be reduced due the additional capacity between the I2C lines and must be adjusted in the software.
We have used a shielded 5x0.14mm² cable, whereby one wire has not been used. The used cable is called: Lapp Kabel Unitronic LiYCY, 5x0.14, article number 0034305. (https://products.lappgroup.com/online-catalogue/data-communication-systems/low-frequency-data-transmission-cables/din-colour-code/unitronic-liycy.html)
The shield is only connected to the Base Station to prevent ground loops.

The distance between the sensors on both boards should be 10mm. Our PCBs have a thickness of 1.6mm, so the printed spacers have a height of 8.4mm (10mm-1.6mm). The CAD of the spacer is located in:
...\1_HallSensor\11_Hardware\112_CAD Files\SensorHead The hole in the center of these spacers (diameter 2.5mm) is the core hole of an M3 thread, which was cut after printing.

Figure 3: Structure of the Sensor Head

The following procedure made sense for the mechanical assembly:
1. 3D printing of the spacers
2. Screw the 2 boards together.
3. Soldering silver wire (connection between the two PCBs). The front pads of the connector are intended for this purpose.
4. Soldering the cable to the top PCB
5. Attach cable ties for strain relief

8

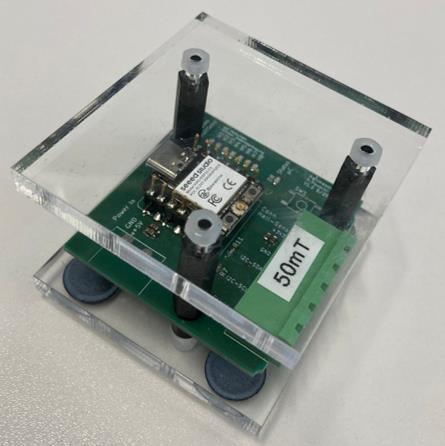
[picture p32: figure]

Instructions to setting up the Hall sensor

2.2.2 Base Station
For us, it was enough to protect the Base Station with 2 plastic covers (against short circuits when something is placed on it, as well as simple ESD protection), see Figure 4.

Figure 4: Base Station with 2 Plexiglas covers. Here 4mm thick.

The CAD of the covers is located in:
…\1_HallSensor\11_Hardware\112_CAD Files\Base In our case, we laser-cut the covers. However, it can also be 3D printed or the sensor can be installed in a proper casing.

## 3 Embedded software (C++ code using Arduino IDE)

3.1 General

Using the Arduino IDE is a very good way to program the ESP32 microcontroller as easily as possible. The source code (C++, extension .ino) is located at: ...\1_HallSensor\12_Software\ArduinoCode_Seeed_XIAO_ESP32_50mT The source code is commented in detail; therefore, we forego a detailed description here.
The most important parameters that you can use & adapt are the following in the file "ArduinoCode_Seeed_XIAO_ESP32_50mT.ino":
- const long i2cclock = 100000;
Baud rate of the I2C protocol. If you have difficulties with the communication between the Hall sensors and the microcontroller, you can reduce the baud rate here (e.g. to 65k).
The following applies for I2C: Baud rate = bus frequency
- const float Hall_Sensitivity = Hall_Sensitivity_500;
The software does not automatically recognize whether a 50mT, 100mT or 200mT Hall sensor is connected. You can set this here.
50mT variant: Hall_Sensitivity = Hall_Sensitivity_500;
100mT variant: Hall_Sensitivity = Hall_Sensitivity_1000;

9
Instructions to setting up the Hall sensor

200mT variant: Hall_Sensitivity = Hall_Sensitivity_2000 = 1.0 (currently Hall_Sensitivity_2000 is not defined)
- const int Repeat_Steps = 1000
Number of internal averages of the measured value of all 8 sensors
- const long baud_rate = 115200;
Baud rate of the serial connection with your PC. We wouldn't change it, but maybe it's necessary for you if your PC software can't keep up

After a successful measurement, the data are built to the following string, which is transmitted serially in a single line (here without an external field):

H1;Bx=-0.066700(-1);By=0.030600(-6);Bz=0.757450(29);Temp=23.759716;ND=1000 |H2;Bx=-0.197575(-11);By=-0.156925(-6);Bz=0.454975(18);Temp=23.677210;ND=1000 |H3;Bx=-0.070525(15);By=0.232950(13);Bz=0.416950(17);Temp=23.482048;ND=1000 |H4;Bx=-0.048675(-16);By=0.013850(-14);Bz=0.297500(12);Temp=23.686794;ND=1000 |H5;Bx=0.008625(-2);By=0.019700(14);Bz=0.199800(7);Temp=23.779552;ND=1000 |H6;Bx=-0.144675(-5);By=0.125450(1);Bz=0.418250(20);Temp=23.450268;ND=1000 |H7;Bx=-0.098025(-6);By=-0.017600(-3);Bz=0.279500(13);Temp=23.851807;ND=1000 |H8;Bx=-0.113375(9);By=0.157375(7);Bz=0.764075(29);Temp=23.389668;ND=1000

The values directly after "Bx", "By" and "Bz" correspond to the measured value in mT. The last raw value (used for debugging) follows in brackets. The temperature (in °C) is used for calibration (Hall effect is temperature-dependent). ND (newData) indicates how many data points could be successfully transmitted and averaged. This value should correspond to "Repeat_Steps". If not, the I2C bus speed should be reduced.

3.2 Installation ESP32 Environment

A new library must be installed in the Boards Manager so that ESP32 chips can be programmed and flashed using the Arduino IDE:
You can find official instructions here: https://support.arduino.cc/hc/en-us/articles/360016119519-Add-boards-to-Arduino-IDE

We have used the following library:
esp32, V3.0.7 by Espressif Systems

3.3 Flash

To successfully flash the microcontroller, the correct board and port must be selected.
You can find the port (in Windows) using the Device Manager under Ports (COM & LPT), e.g. “COM10”. You must select the following board: "XIAO_ESP32C3"

Flashing takes about 1 minute, whereby the project is built and compiled beforehand.

10 Instructions to setting up the Hall sensor

## 4 Calibration

The Hall sensors have small tolerances between each other due to the manufacturing process. As we want to use all 8 sensors to measure the magnetic field, the deviations between the sensors should be as small as possible.
Calibration makes it possible to align the sensors and thus achieve a better measurement result. If only a single sensor were used, this would not be necessary, as the relative accuracy between 2 measurements is really good for modern Hall sensors (however, NMR-based sensors are senseful for absolute accuracy).

A cylindrical coil was built for the calibration, as the magnetic field can also be precisely determined by a precise current measurement. The cylindrical coil has 2 layers: A continuous winding (1st layer) generates the main magnetic field. An additional winding at both ends (2nd layer) homogenizes the magnetic field in the center.

However, please note that calibration is not absolutely necessary! If calibration is not possible for you, then you can skip the following steps.
Avoiding calibration increases the error in the magnetic field mapping, but this may be compensated for by the interpolation between the measuring points implemented in the analysis of the measurements. However, the result has not been evaluated by us and should therefore be checked.

4.1 Software to calculate magnetic field

4.1.1 Analytical Solution using Biot Savart

- General
The analytical calculation was written in Matlab and is available at: ...\2_Calibration\21_Hardware\211_CalibrationSolenoid_Analytical

The magnetic field is calculated using the analytical formula according to Simpson et al (https://ntrs.nasa.gov/api/citations/20010038494/downloads/20010038494.pdf) by placing round conductor loops parallel to each other.

The software for calculating the magnetic field is being run iteratively. The following procedure made sense to us. This could be automated in a further development:
1. With "Main_CalculateSolenoid.m" the magnetic field in the center of the cylinder is calculated, depending on the parameters you have set. At this point we don’t know the optimal number of turns of the 2nd layer and we estimate it (e.g. 25). We try to determine the optimal cylinder geometry (diameter, length) and the copper wire diameter with which you can achieve the desired field strength at the desired current (limited e.g. by available current sources)
2. In the "getOptimumSecondLayer.m" script, the parameters (diameter/length of cylinder, copper wire) must have the same values as in 1). The script then calculates the optimum number of turns of the 2nd layer.

3. Insert the calculated number of turns back into 1) and check whether the calculated field strength and homogeneity are correct.

The software is intensively commented, which should make adaptation possible.

We used a DN160 KG pipe (radius 80mm) as the cylinder core. 290 windings were on layer 1. The insulated copper wire has a diameter of 1.5mm, plus 30µm enamel thickness. This results in a cylinder length of 452.4mm. The 2nd layer has 27 turns.

4.1.2 FEM Simulation using free Software FEMM & Python
The analytical simulation is very fast, but only assumes the conductor loop as an ideal path. This error can be checked again in a FEM simulation. The open source tool FEMM V4.2 with the Python interface pyFEMM is used: https://www.femm.info/wiki/pyFEMM
The Python code is located at:
...\2_Calibration\21_Hardware\212_CalibrationSolenoid_FEM

The software is commented in detail so that it can be easily customized. Essentially, the Python script calls the FEMM software in the background, sets up the geometry, adds the material parameters and the flowing current, starts the FEM simulation, reads out the result and saves it in a CSV table (for further processing).

We have found that pyFEMM can become unstable if too many windings are built up in FEMM. Therefore, the entire simulation was split into 8 individual FEM simulations and the results were super positioned at the end.

4.2 Structure of the hardware

The CAD of the cylinder coil is in: ...\2_Calibration\21_Hardware\214_CalibrationSolenoid_CAD_STEP

the assembly is divided into 2 parts:
- Cylinder coil (water-cooled)
- Slider (mounting of the Sensor Head)
- Current measurement setup for calibration and is described below

4.2.1 Cylinder
The cylinder is shown in Figure 5.

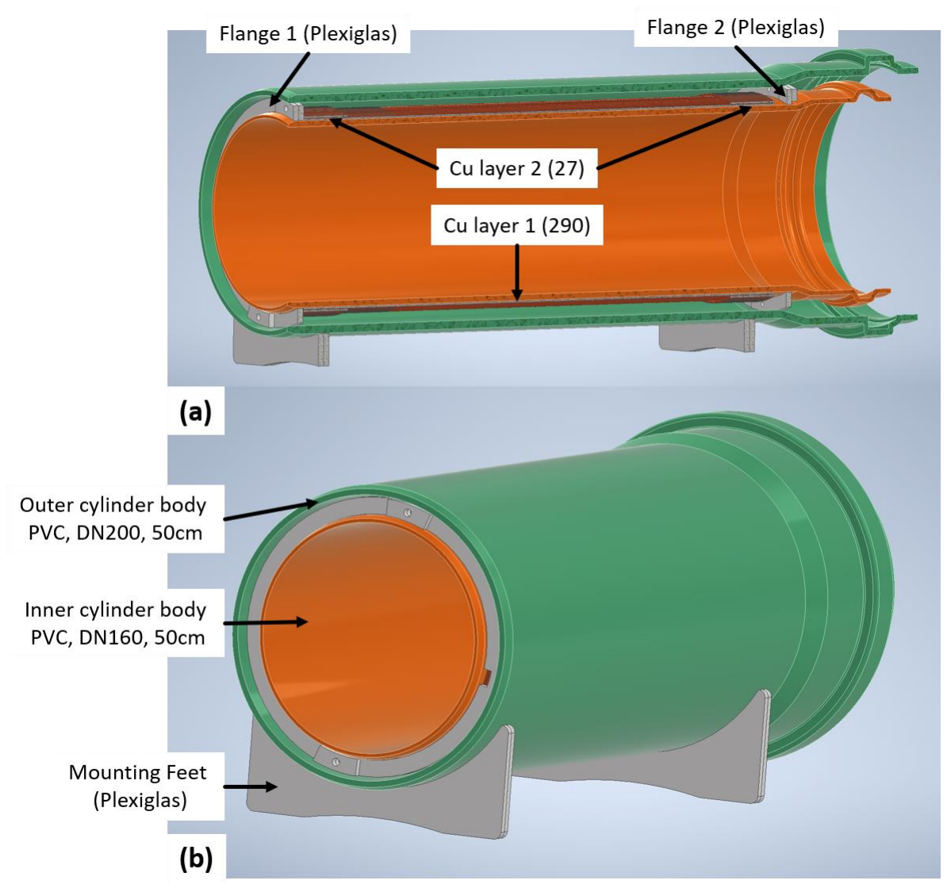
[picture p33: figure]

Figure 5: CAD rendering of the assembled cylindrical coil

- Inner Cylinder
An ordinary waste water pipe is used. We bought this pipe:
Ostendorf Kunststoffe, No. 222000, KG EM Rohr SN 4 Coex DN/OD 160 x 500 mm https://www.ostendorf-kunststoffe.com/en/products/waste-water-pipes/the-kg-system-pvc/
- Outer cylinder
The electric coil becomes hot very quickly due to losses. It is therefore water-cooled (as heat capacity). The coil is sealed with a second waste water pipe:
Ostendorf Kunststoffe, No. 223000, KG EM Rohr SN 4 Coex DN/OD 200 x 500 mm https://www.ostendorf-kunststoffe.com/en/products/waste-water-pipes/the-kg-system-pvc/

To be able to seal flange 2 properly, the end is shortened slightly with a saw (Figure 6). A small hole (1 mm) was drilled into the top of this cylinder to release the pressure from the cylinder when the temperature increases (and thus the volume expands).

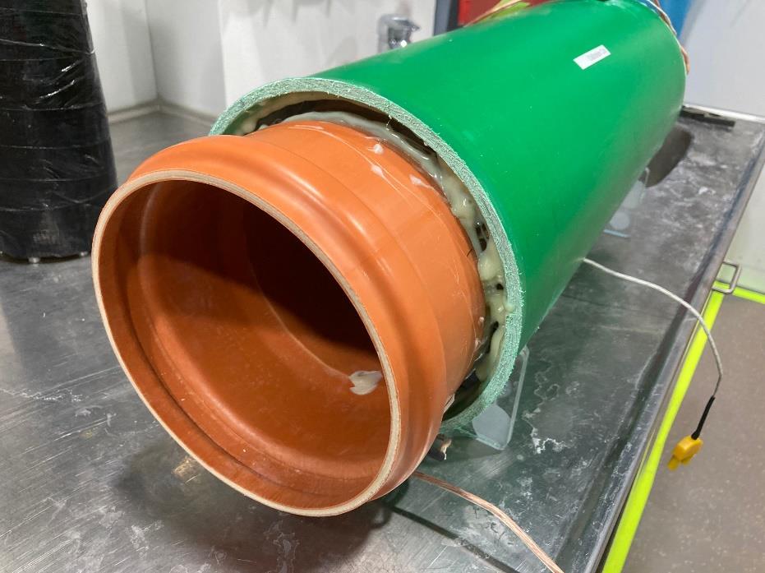
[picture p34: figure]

Figure 6: Photo of the coil

- Flange 1 (Front)
The flange consists of 3 plastic parts, see Figure 7. In our case, everything is laser-cut from 5mm thick Plexiglas. But the parts can also be 3D printed or milled from other materials.
Two holes are provided here for the water inlet and outlet. An M6 thread is cut into these after lasering. During the measurement, the volume is sealed with a plastic screw, a washer and an O-ring (under the washer) (Figure 7c). The Reinforce part was fully glued to the base. The adhesive used was 2K epoxy Loctite EA 9466 (RS-Online 244-2026) (https://de.rs-online.com/web/p/klebstoff/2442026?gb=s) (slightly yellow in the photo), as the adhesive stays a bit elastic when cured and is therefore better able to withstand temperature fluctuations. The same adhesive was used to glue the flange to the cylinders over the entire surface. The PVC of the cylinders must be properly sanded, otherwise the glue joint can hardly withstand any load.

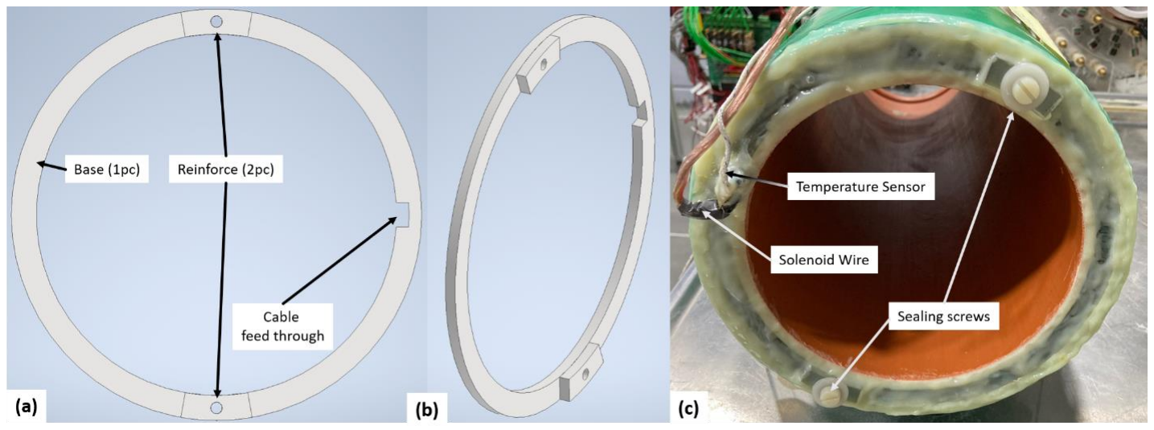
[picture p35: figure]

Figure 7: Flange 1 (Front)

- Flange 2 (Back)
The rear flange has a slightly different design (see Figure 8). We broke this part when winding the cylinder coil (see details later), so it is designed to be "replaceable" (as it can’t be pulled over the thick flange of the waste water pipe) in case it breaks during winding and needs to be replaced.
The base is divided into 2 parts (can be placed around the cylinder afterwards). The 2 halves are connected (not glued) using the Reinforce parts. They are screwed together with M4 plastic screws (length 16mm). Once everything is assembled and the cylinder needsto be sealed, everything is sealed with plenty of glue.
All parts are laser-cut from 5mm plexiglass. Any other manufacturing method is possible too.

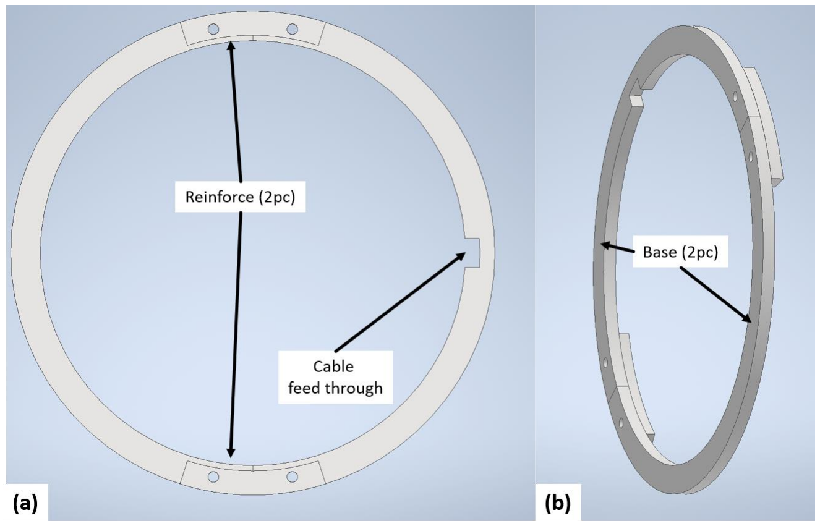
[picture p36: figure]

Figure 8Flange 2 (Back)

- Mounting Feet
In our design, each foot consists of 2 pieces of 5mm thick Plexiglas sheets (for a larger gluing surface with the sanded PVC cylinder).
- Cu Layer 1
We used a large lathe to wind the coil. The end without the flange of the water pipe was clamped in the chuck. An original DN160 cover cap was installed in the flange itself (Ostendorf Kunststoffe, No: 222620, KGM Muffenstopfen DN/OD 160), in which the center point of the lathe was inserted.

Flange 1 was mounted directly at the beginning (in the direction of the chuck) to enable a clean stop for the windings (see Figure 9).

The coil was turned at the slowest speed of the lathe, keeping the copper wire under tension and ensuring that the windings were as tight as possible. After reaching the correct number of windings, flange 2 was mounted and the wire was fed through the feed through and cut off.
A temperature sensor (type K, RS-Online 136-5868) (https://us.rs-online.com/product/rs-pro/1365868/71083665/) was glued to the coil in order to detect an excess temperature during operation.

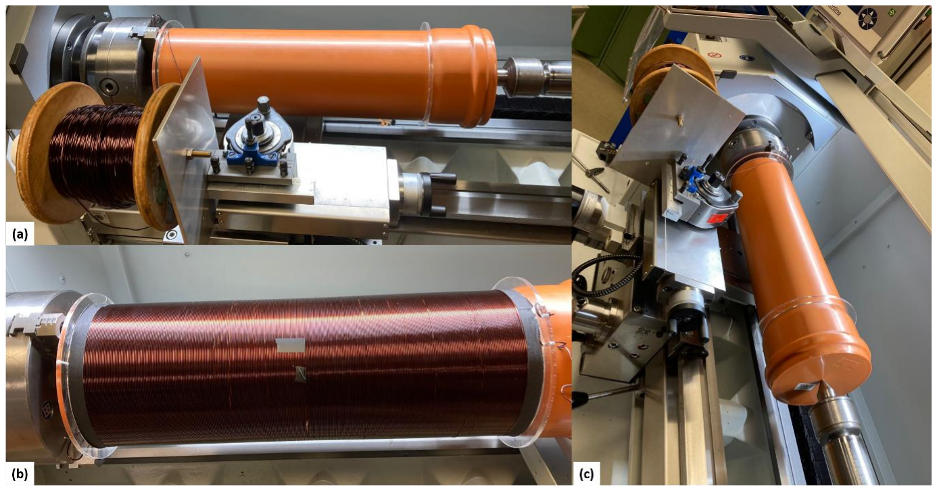
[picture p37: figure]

Figure 9Winding layer 1 on the lathe

- Cu Layer 2
Layer 2 is wound in the same way as layer 1. Make sure that the winding direction for layer 1 is retained. The 3 windings are then interconnected (see diagram in Figure 10).

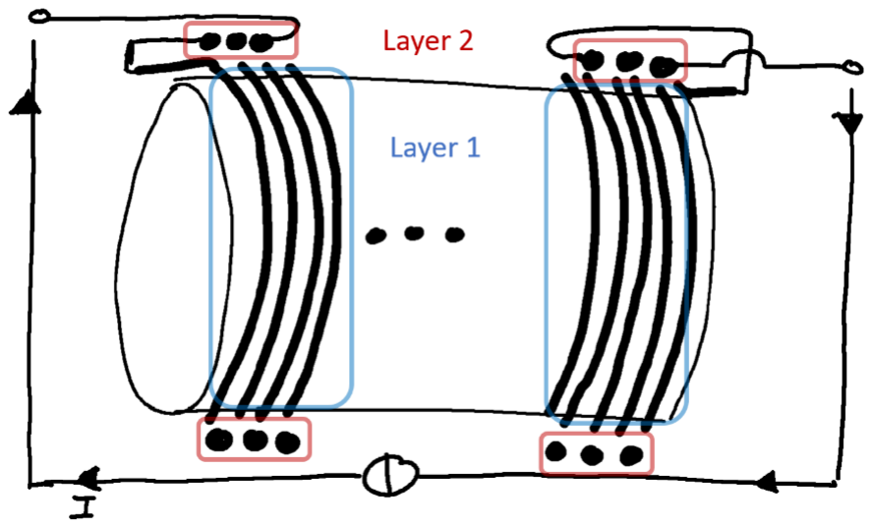
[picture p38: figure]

Figure 10Interconnection of layer 1 and layer 2

After both layers were wound up, the electric coil was wrapped with adhesive tape and secured in this way.

4.2.2 Slider
The slider (see Figure 11a) is inside the solenoid and holds the Sensor Head in the isocenter of the solenoid. To measure all 3 axes individually, the sensor can be mounted in different positions (Figure 11b). The slider consists of many parts and the assembly is explained below.

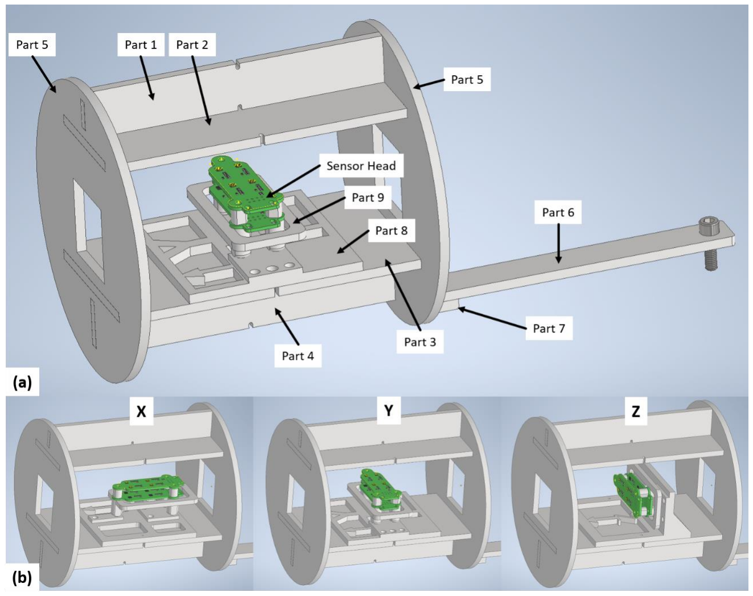
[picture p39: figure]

Figure 11(1) CAD Picture of used slider. (b) Mounting of Sensor to measure different axes

- Part 1-5
The main body of the slider is again made of laser-cut 5mm thick Plexiglas. These 6 parts (2 times Part5 is used) were assembled with superglue. Any other glue will also work
- Part 6
Plexiglas, 5mm thick, laser-cut. This part is the spacer that holds the slider in the isocenter (using the plastic screw that rests on the edge of the cylinder).
- Part 7
3d printed angle. Glued to Part 5. Part 6 and Part 7 are connected via a bolt (screw)
- Part 8 and 9
3D printed holder for the Sensor Head, with which each of the 3 axes can be individually calibrated for the 8 Hall sensors. Hall sensors 1 and 2, H3 and H4, H5 and H6, H7 and H8 were measured simultaneously, as the homogeneity of the cylinder is good enough.

Part 8 is centered with Part 3 via M2 screws (in the holes). Additional rubber bands have firmly connected the parts together.

The Sensor Head is screwed to Part 9 (M3 thread cut into Part 9). This assembly is again attached to Part 8 using rubber bands. Self-adhesive cable clamps were attached to the sliderto have attach points for the rubber bands (RS-Online 184-2343). (https://de.rs-online.com/web/p/kabelclips-und-klemmen/1842343)

4.2.3 Current measurement and operation of the cylinder coil
The setup of the current measurement is also described in the SI of the paper. Therefore, only a brief scheme in Figure 12. Figure 13 shows pictures of the measurement.
The setup depends heavily on the hardware you have available (shunt, relay, multimeter). The shunt should be sufficiently well cooled so that the resistance does not drift due to temperature changes. The relay can also be replaced by a powerful switch, or is unnecessary if a sufficiently powerful power source is available. A "normal" relay is also possible (we only had a solid state relay left).
Make sure that the multimeter is sufficiently accurate in the expected voltage range (<1V). A communication interface is advantageous so that calibration can be automated. With the one we used (GW-Instek GDM-8255A), this was possible via USB and serial interface. For powers up to 30A/60V we had 3 lab voltage sources (EA-PS 3065-10B) in parallel operation (indicated in Figure 12). For higher currents, we used 8pc 12V-batteries connected in series (at charging end voltage 110V/69A), see Figure 13.
If you also want to use the battery solution, make sure to prevent the batteries from short-circuiting! A DC electric arc is difficult to switch off again!

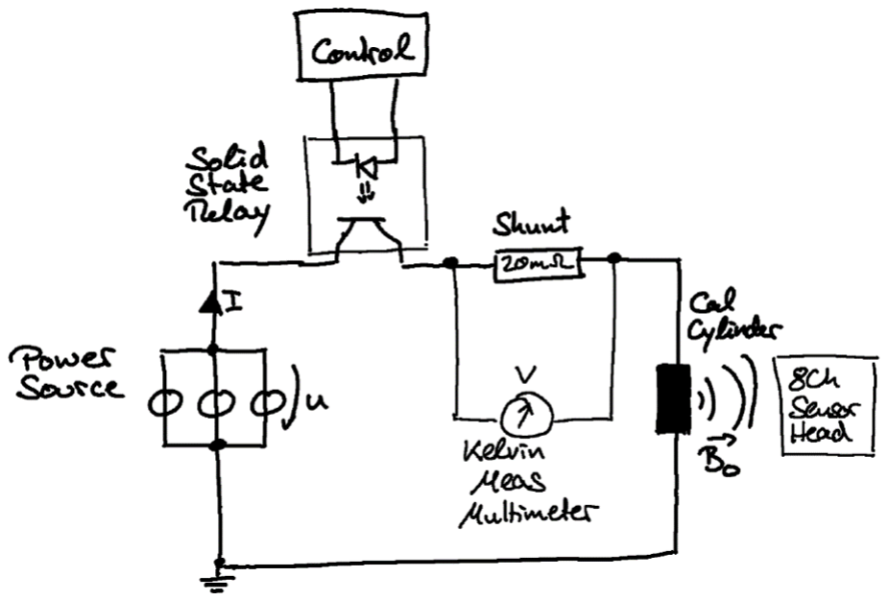
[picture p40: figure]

Figure 12: Schematic diagram of the current measurement

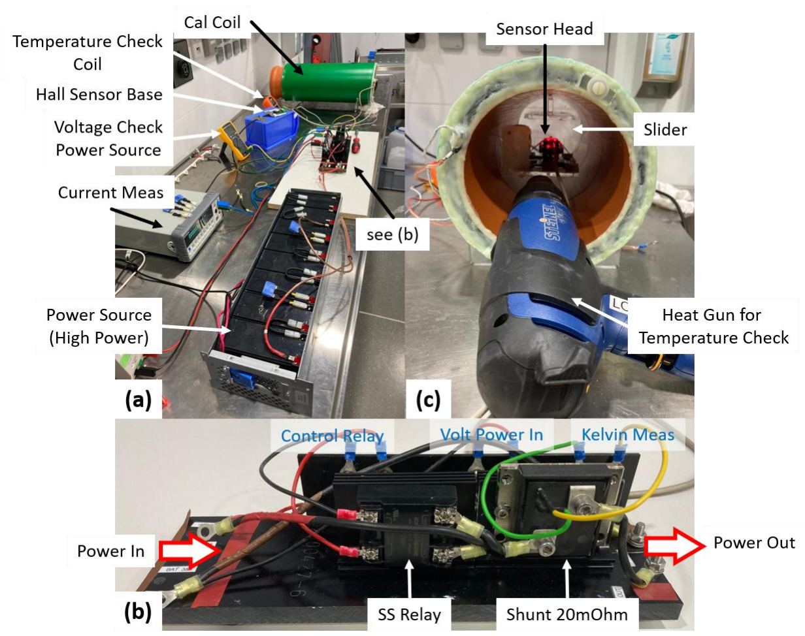
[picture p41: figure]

Figure 13: (a) Operation of the coil during a calibration sequence. In this case, the 8 serial 12V batteries generate the current flow. (b) Set-up of the current measurement. (c) Sensor Head in the cylinder. Hot air gun for temperature change of the Sensor Head.

- Alternative current measurement
Multimeters are probably available in every electrical laboratory. However, access to a multimeter with a communication interface can be difficult. In particular, we had difficulty finding a multimeter with which communication was "easily" possible (without the need for special/expensive toolboxes, licenses, etc). We were lucky that with the GW-Instek we happened to already have one that could be read out serially.

If you have major difficulties at this point, the following solution could be useful. The setup is shown schematically in Figure 14.

Based on an Arduino (no matter which model - for example the Arduino Uno, which is used in the robot controller) and an external 16bit ADC, you can build a precise system:

The | external | ADC | ADS1115 | from | Adafruit | Adafruit
(https://www.adafruit.com/product/1085#technical-details, Mouser Number: 485-1085) is an I2C adjustable ADC with 16 bit and adjustable gain. This is a suitable library for the Arduino IDE: https://github.com/adafruit/Adafruit_ADS1X15

You can find more details on setting up the ADC in this tutorial:

https://learn.adafruit.com/adafruit-4-channel-adc-breakouts/

You can use the "continous" sample script:

https://github.com/adafruit/Adafruit_ADS1X15/blob/master/examples/continuous/continuous.ino

As far as we can tell (we have not used the system), you hardly need to change anything in this script. What we would recommend:

- Line 23: Changes the serial baud rate to 115200 Bd
- Line 24/26/27: Serial texts for start could be deleted (optional)
- Line 38: Remove comment / activate "ads.setGain(GAIN_FOUR);"
- Line 64: Clean up serial text. Replace this line with: "Serial.println(ads.computeVolts(results));"
Then the serial output of this system corresponds to the multimeter we are using and you hardly have to change anything in the following scripts.
- Line 70: delete delay(1000). A hardware interrupt is used so that a serial string is sent out with each new ADC sample. The sample rate is 860Sps, so you get a new serial measurement every ~1.2ms

This accuracy results in a maximum precision of 1bit = 0.03125mV. Depending on the shunt used, you can calculate your maximum resolution. In our case, this results in a current resolution of ∆I = ∆V ⁄R = 1.5mA or, with the calibration coil used, a resolution of the magnetic field of approx. 1.2µT. Of course, additional noise is to be expected.

This ADC board costs approx. 14€. If an already available Arduino is used (e.g. the Uno from the robot controller, or a cheap Nano etc), a very inexpensive & integrated system can be set up.It makes sense to check the performance with an industrial multimeter.

A separate PCB is actually not required for this setup. For reliable operation, however, the PCBs should be installed in a casing (i.e. to strain relief the cables).

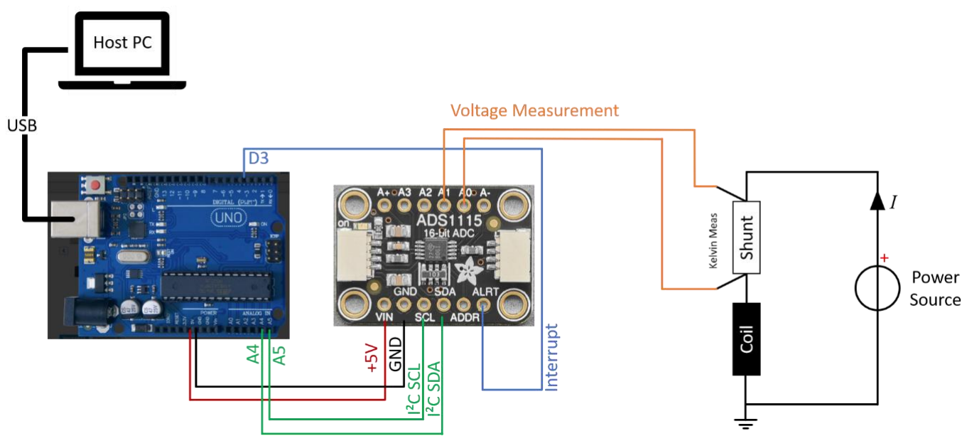
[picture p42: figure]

Figure 14: Possible setup of your own "multimeter" using an Arduino UNO and the Adafruit board (16bit ADC ADS1115)

4.3 Calibration Run

4.3.1 Procedure
In our case, 3 experiments were carried out to calibrate the Hall sensors:
1. Linearity in a varying magnetic field (Ch. 4.3.2)
2. Temperature dependence in the static magnetic field (Ch. 4.3.3)
3. Static offset (Chap. Ch. 4.3.4)

4.3.2 Calibration Run: Linearity

- Position/Rotation Sensor Head
Each axis for each sensor is calibrated individually, whereby Hall sensors 1 and 2, H3 and H4, H5 and H6, H7 and H8 are each measured together (see example for x-axis in Figure 15). This means that 8 measurements are taken per axis (a total of 3x8 = 24 individual measurements).

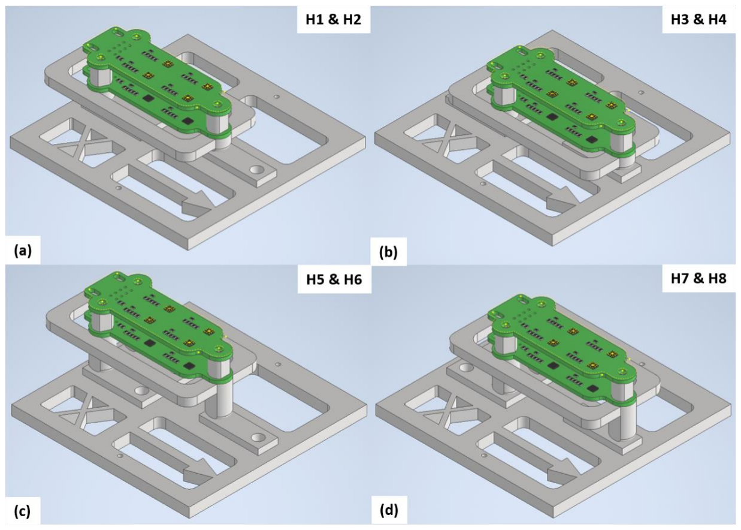
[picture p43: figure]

Figure 15: Example of positioning the Sensor Head for calibrating the X-axis. (a) Hall sensor H1 and H2 are in the isocenter.
(b) ... (d) All 4 positions for calibration.

The feet of the Hall sensor holder are self-centering. This means that the user must ensure that the Sensor Head rests firmly (and is not jammed in any way). The magnetic field of the cylinder is rotationally symmetrical, so the rotation of the slider is not critical.
However, it is important to note that the measurements are carried out in a normal laboratory room. There are therefore influences from other devices/earth magnetic field etc. Therefore, the calibration cylinder should be in the same position during all measurements (we used an edge in the table for this and aligned the cylinder to it).

- Used Software
The Matlab software for carrying out the linearity measurement can be found here: ...\2_Calibration\22_Software\221_Matlab_ReadOut_DuringCalibration The script "Main_Calibration_Linearity.m" is used. The software is commented in detail, hence the reference to the source code.
The most important changes before your experiments are:
Depending on your multimeter, you will need to change the type of communication and how the measured values are tapped. To do this, adapt the "FunctionGetCurrent" function so that the "Volt_Meas" variable gives the measured voltage in volts. This is accompanied by an adaptation of the "% SetUp Communication with Multimeter" block in the main program

Immediately before the experiment (setup the script):
Adjusts the LogFile and all SetUp parameters for documentation (e.g. Multi_R_Shunt, Shunt_Type, HallSensor_Type etc).

During experiment:
Parameters:
- num_AQ: Number of measured points at the same magnetic field strength (for more precise calibration)
- num_BField_Steps: Number of measured magnetic fields per axis & sensor
- measured_Sensor: Specifies which sensor is currently being measured (as string "H1"). In each case 2 sensors are measured simultaneously. Enter the smaller index here
(e.g. for H1 and H2 -> 'H1')
- measurend_Direction: Specification of the momentary measured axis as a string ("x", "y", "z")

Start the script. It establishes the connection to the Hall sensor and multimeter. And then immediately evaluates the first measuring point. Once the measurement is complete, this is indicated in the command line. The measurement points are stored temporarily in the "LogFile" struct. After the experiment, the file is saved to the hard disk.

- Current change
We took 26 measuring points per calibration run. The 3 parallel voltage sources (in CC mode) were used for currents up to ±30A. For higher currents, the battery bank was used (once connected as 7seriell and once as 8seriell).

The software signals when the current can be changed. The current flowing is then changed manually (adjusting the power sources). As soon as the current flows, this is reported to the still running Matlab script (push “Enter” in the command window) and the measuremnt is done at the next magnetic field. Of course, this can be automated in a subsequent development.
A lot of ohmic power loss occurs during the measurement and heats up the copper considerably, especially at high power levels (our coil has approx. 1.6 Ohm -> 40A leads to 2.5kW). Using the temperature sensor, make sure that the coil temperature does not exceed 60°C (approx. value, protects the copper insulation and the plastic used). Care should be taken to ensure that the Hall sensor does not become too hot.
If it exceeds this temperature: Wait until it has cooled down (takes a long time). Or replace the cooling water with cold water via the built-in threads in the front panel.

4.3.3 Calibration Run: Temperature Dependence
The Hall effect is highly temperature-dependent. A large part of this error is already corrected by the integrated electronics in the Hall sensor IC itself. However, the Hall sensor heats up due to the losses in the cylindrical coil. Therefore this experiment.
The script "Main_Calibration_TemperatureDep.m" is used. In principle, there is no difference to the instructions in the script in 4.3.2. The only difference is that several iterations are not run through and the parameter "num_AQ" is significantly larger (e.g. 100). Set a constant magnetic field (in our case 20mT) and start the measurement.
During the experiment, we raised the temperature to 40°C using a hot air gun (see Figure 13c).

This measurement is carried out simultaneously for all Hall sensors per axis. The associated error (due to inhomogeneity) is compensated for in the calibration calculation by a weighting factor. During the measurement, mount the Sensor Head in the position of Hall sensor H1 and H2 for all 3 axes.

4.3.4 Calibration Run: Static Offset
This step only makes sense if you have access to a Zerofield Chamber. In our case we had access to one, where other experiment are carried out. Or you have access to a small one, like the ones typically used for other magnetic field sensors (like this one). (https://www.magnetic-shield.com/mini-zero-gauss-chamber/)

The "Main_Calibration_ZeroOffset.m" script is used for the measurement. Here you only have to adjust the COM_Port for your Hall sensor. The rest is done automatically.

4.4 Evaluate Calibration & get Calibration Parameter

The scripts for the evaluation are available at:
...\2_Calibration\22_Software\222_Matlab_Calibration Copy all logged measurement data from the calibration into the "Log_Folder" folder. All measurement files from this folder are evaluated together in the script.
The magnetic field of the calibration cylinder is not perfect due to geometric errors. This is shown for example by the fact that the calculated calibration factors of the sensors are outside the data sheet specification. Therefore, the static error of the calibration cylinder is first determined and minimized using the data sheet specification. Use the script "Main_PostProcessing_Calibration_calcCalError.m" for this.

Nothing needs to be changed by you. The functionality of the software is intensively commented. The evaluation takes a while (running through many fmincon optimizations).

At the end, 3 figures are created, whereby plot 2 is used to evaluate the error of the calibration coil (see Figure 16). We take advantage of the fact that the Hall sensors are tested by the manufacturer and produced within certain tolerances.
The upper plot shows for each axis how many sensors exceed this manufacturer tolerance for an assumed coil error. We set the first data point at which the x and y axes have an error of 0 as the error of the calibration coil. In our experiment, the z-axis error then increases, which could be explained by the larger manufacturing tolerance at this axis. We have chosen -4.2% as the error.

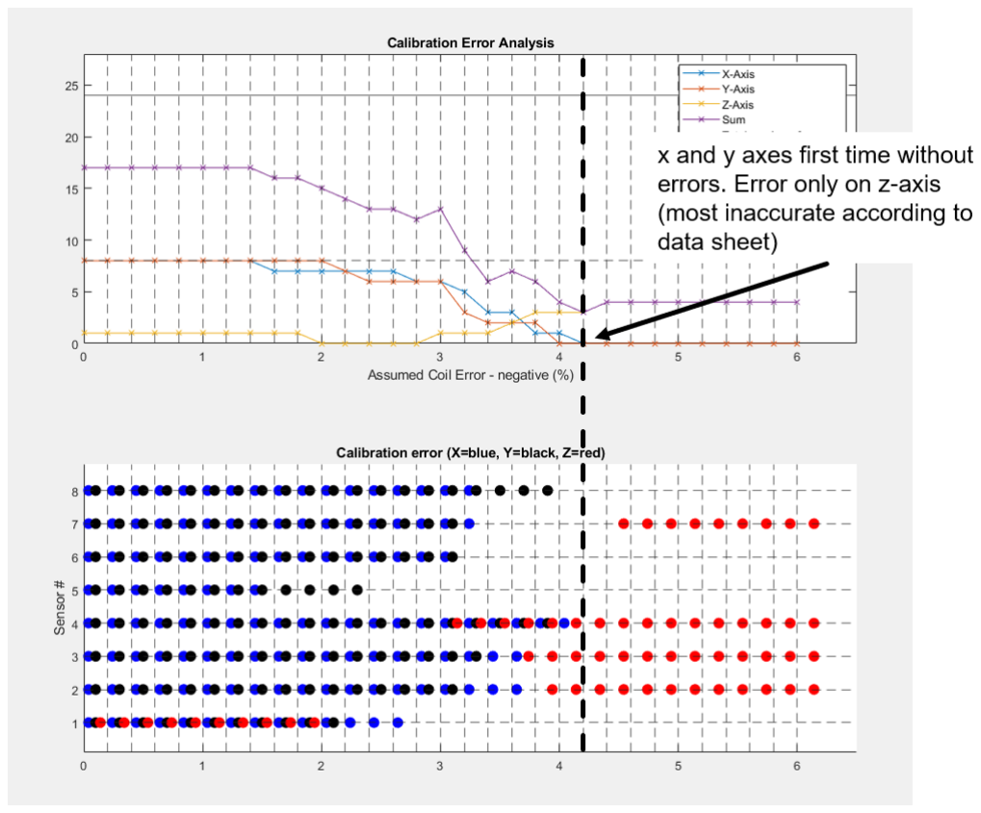
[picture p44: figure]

Figure 16: Exemplary result of the error estimation

This value is then transferred to the "Main_PostProcessing_Calibration.m" script as the "error_CoilConversion" parameter.
The script runs automatically. The calculated calibration factors (struct CalFile) are saved in a file at the end (e.g. "Calibration_50mT_24-Jul-2024_19_02_55.mat").

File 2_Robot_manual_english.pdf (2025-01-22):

## Instructions to setting up the

# Robot

Project

Easy Scalable, Low-Cost Open Source Magnetic Field Detection System for Evaluating Low-Field MRI Magnets using a Motion Tracked Robot

Pavel Povolni

October 2024

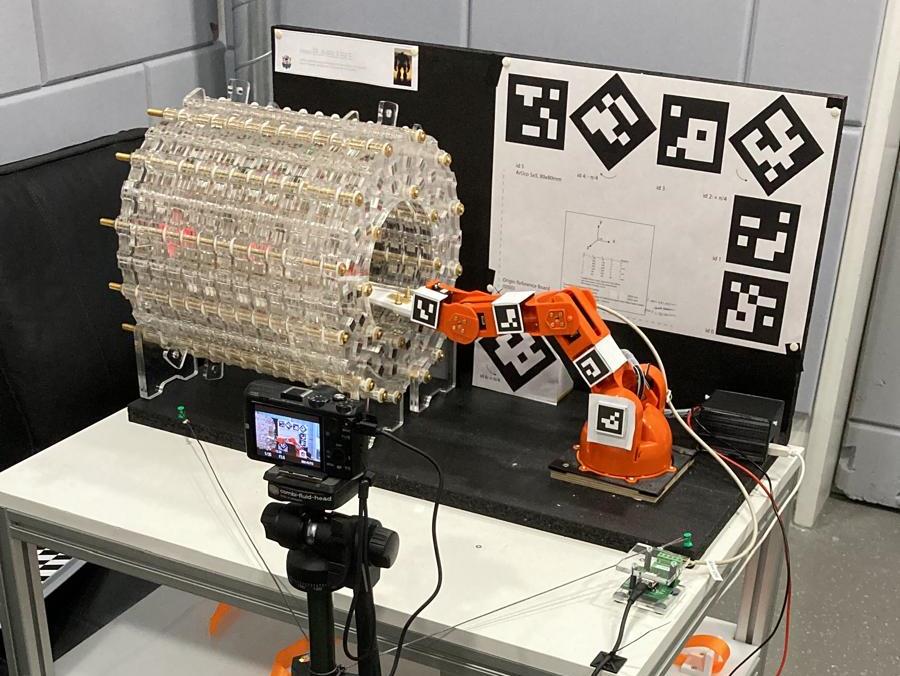
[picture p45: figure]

Instructions to setting up the Robot

## Content

1 | Preamble | 3
2 | Mechanical Design Robot | 3
2.1 | Design of used Robot (Arduino Tinkerkit Braccio) | 4
2.1.1 | Tinkerkit Braccio | 4
2.1.2 | Sensor Head Holder | 5
2.1.3 | Extract Translation for Motion Tracking | 5
2.2 | Hardware for ArUco Robot Marker | 5
2.3 | Hardware for base sensor | 6
2.4 | Environment / Assembly | 7
3 | Custom Electronics | 8
3.1 | Power Electronic Driver | 8
3.2 | Base sensor | 10
4 | Embedded software | 10
4.1.1 | Library | 11
4.1.2 | Usage (Serial Commands) | 11
5 | Calibration of Base Sensor | 12
5.1.1 | SetUp | 12
5.1.2 | Evaluation / Linearization | 13

## 1 Preamble

These instructions describe the setup, start-up and calibration of the robotic arm.
Further information can be found in the publication, as well as in the Appendix and Supplementary Information referenced there.
Software used:
1. PCB design: KiCad 7 (Free)
2. Mechanical design (CAD): Autodesk Inventor 2022 (Commercial). All parts exported as .Steps
3. Embedded software: Arduino IDE 2.2.1 (free)
4. Calibration: Matlab 2021b (w/o expensive toolboxes)

If you have any further questions, please contact us!

## 2 Mechanical Design Robot

You can find the hardware under: …\3_5DoF_Robot\31_Hardware

The entire mechanism is shown in the following Figure 1:

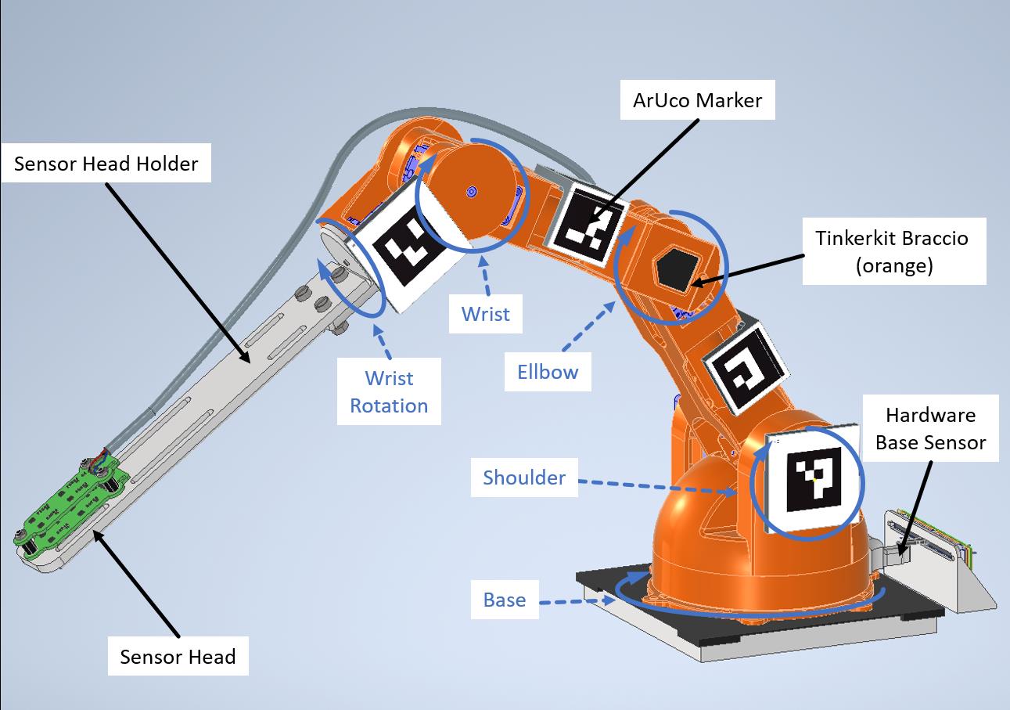
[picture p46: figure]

Figure 1: Complete mechanics around the robot (not shown: PowerElectronicDriver housing and motor wiring)

2.1 Design of used Robot (Arduino Tinkerkit Braccio)

We used the Arduino Tinkerkit Braccio (6 Degrees of Freedom) robotic arm for our experiment: https://store.arduino.cc/en-de/products/tinkerkit-braccio-robot

There are a variety of possible robotic arms. Cheap ones start at around €20 (search for "robotic arm" on aliexpress.com, for example) and it seems there is no upper price limit (which of course means that the tolerance of the built-in mechanics is getting better and better).
Depending on how big your budget is, we would actually recommend the Arduino Braccio. Either the commercial product. Or printed out by yourself (CAD is open source). If not, the following mechanics and electronics would have to be adapted. We try to describe the needed changes as good as possible.

2.1.1 Tinkerkit Braccio

The 6th degree of freedom is the gripper (open/close), which was not used in our case. We have therefore removed the gripper. Otherwise there are no mechanical changes to the robot itself.
In the experiments, we found that the shoulder motor (see Figure 2) experiences the highest load and 2 problems occur: Firstly, the motor does not manage to reach all coordinates of the FOV (especially the upper ones) due to limited torque. Secondly, the high torque very easily damages the mechanical mount of the motor axis.
You could install a more powerful servo motor, but this is critical because of the space available and the quality of the mechanical mount.
We have therefore decided to add additional relief in form of a rubber band based pre-tensioner (see Figure 2, no CAD as a simple piece of aluminum with rubber bands is used).

To align the robot basis, a template was printed to hold the star-shaped base. The base plate is a 12mm wooden plate measuring 130x130mm.

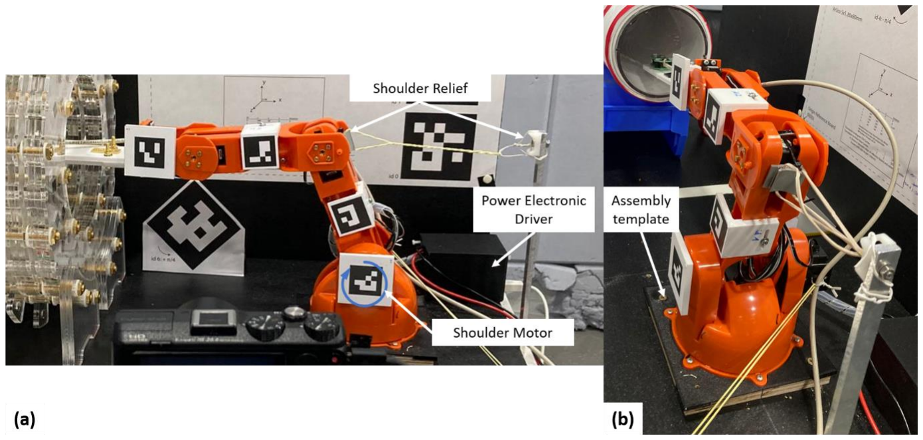
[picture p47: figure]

Figure 2: Tinkerkit Braccio with Shoulder Relief (using rubber band)

2.1.2 Sensor Head Holder
The Sensor Head holder consists of two 3D printed parts. The printing material does not matter, but we have had good experiences with PETG.
Depending on what you want to measure, it is advisable to shorten or lengthen this jib.

The holder is mounted on the robot instead of the gripper. This holder is designed mechanically weak on the robot. Take care not to damage anything.

2.1.3 Extract Translation for Motion Tracking
To calculate the kinematics (calculation of the position of the Sensor Head), the exact dimensions of the robot are required (e.g. distance between the markers and the rotation axes).
This is easy to measure in CAD (see Figure 3). However, it seems it’s not possible to export sketches into STEP, so the sketch is only included in the original files.
Autodesk offers a free education license for the used CAD software “Inventor”. Your institute may be covered by this. If not, you will have to redraw it in your program if you want to change anything. If you set up the robot identically, everything is already stored in the software and evaluation.

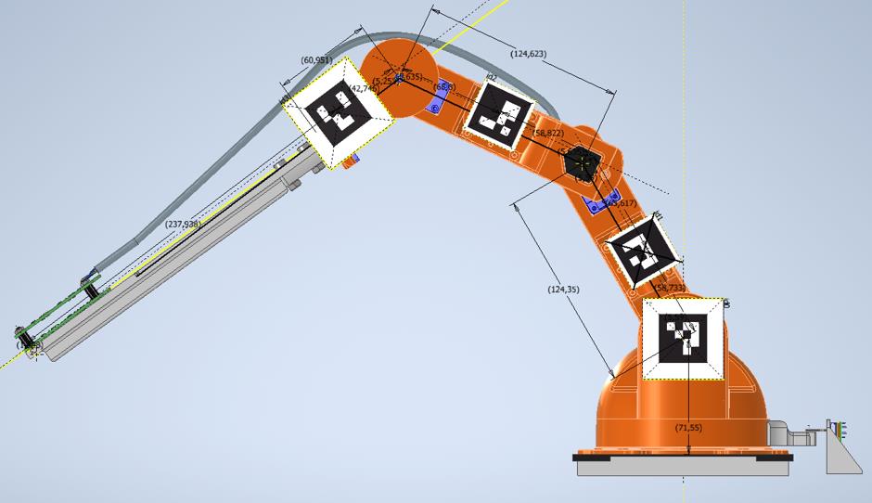
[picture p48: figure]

Figure 3: Sketch of exact translations

2.2 Hardware for ArUco Robot Marker

The holders for the ArUco markers on the robot are in the same folder. The holders are 3D printed. The holders for id1 to id4 are designed so that they "automatically" latch into the correct position with the help of lugs. A small self-tapping screw attaches the holder to the robot. The holder for id0 has a bolt on the back that is inserted into a corresponding hole (axis) of the robot (shoulder axis). Push the holder in as far as it will go.
You can find the ArUco markers used under:
...\4_MotionTracking\41_Hardware\411_ArUcoCodes You can simply print out the markers on paper and gluet them onto the holders. It is important that the orientation of the markers is kept right (see Figure 4. Marker id0 is the wrong in CAD).

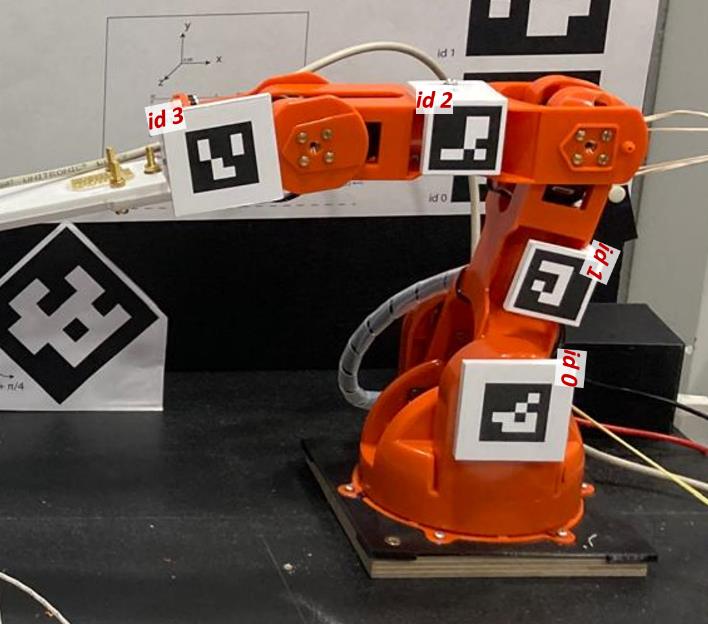
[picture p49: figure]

Figure 4 : Orientation of the robot markers

2.3 Hardware for base sensor

To increase Motion Tracking accuracy, an additional sensor is attached to the base (see Figure 5).

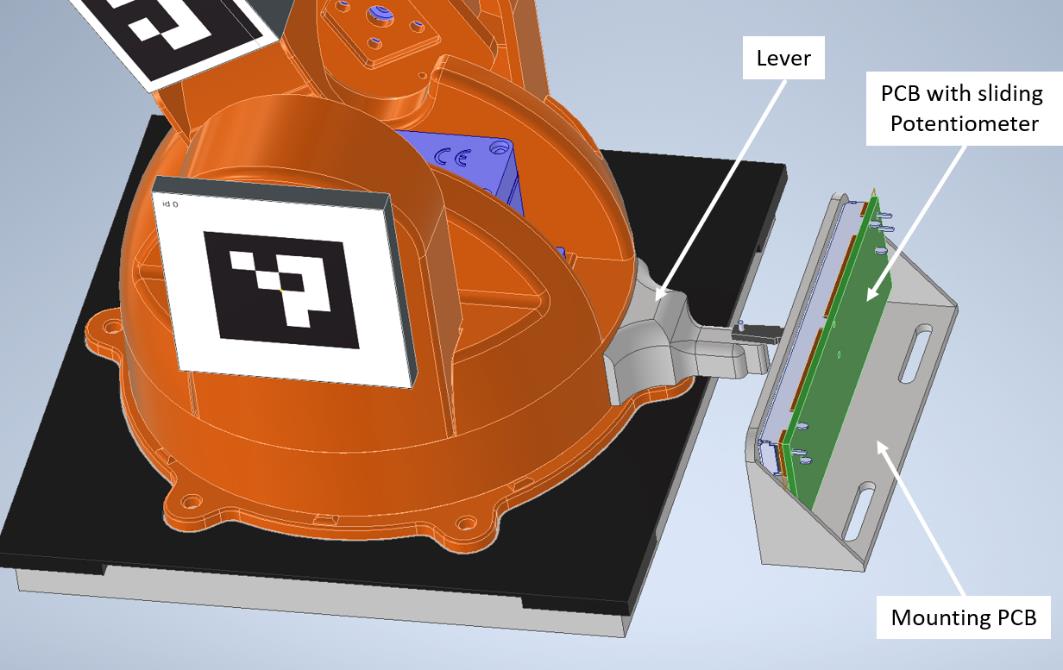
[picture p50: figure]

Figure 5 : Base Sensor Parts

This sensor consists of 3 parts:
5. PCB with sliding potentiometer (see 3.2)
6. PCB holder: 3D printing
7. Lever on the robot base: 3D printing

The lever of the potentiometer must be drilled before the circuit board is fitted:
Center, distance 2mm to the front edge, diameter 1mm.
A 1mm pin (e.g. a 1mm-drill) is glued into this hole (connection to the lever). The assembled PCB is attached to the bracket via the mounting points of the potentiometer.

The lever is glued to the base (sand the plastic beforehand). Make sure that the base of the robot is at 0° (neutral) beforehand.
Now clip the PCB incl. holder into the lever via the pin and align the holder parallel to the baseplate of the robot. Make sure that the potentiometer is in the center position (e.g. can be determined using a caliper).

2.4 Environment / Assembly

The three main components (robot, magnet, ArUco reference) were installed in a reference system (see Figure 6) so that the translation between all components is known. The reference system consists of 2 wooden boards (bottom 750x350mm, rear 750x422mm, thickness 22mm), which are screwed at right angles to each other.

This drawing was created in Autodesk Inventor and unfortunately cannot be exported to STEP (see 2.1.3). The original CAD file is available at: ...\3_5DoF_Robot\31_Hardware\313_EnvironmentCAD_AutodeskInventor

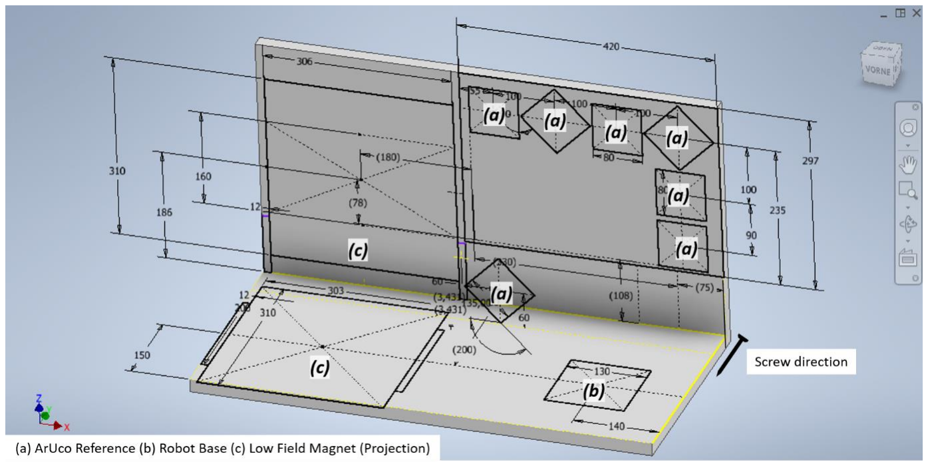
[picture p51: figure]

Figure 6 : Setup of the environment with the position of the robot base, the magnet and the ArUco Reference Board (used as a reference for determining the position of the robot markers)

## 3 Custom Electronics

You can find the PCBs here:
…\3_5DoF_Robot\31_Hardware\315_PCB_ElectronicDrive

2 PCBs are required to operate the robot (see Figure 7). The PCB is two-layered and the design rules are identical to the Hall sensor. To save costs, both PCBs are combined in one layout. Before assembly, the PCB must be sawn apart and separated into 2 PCBs (simultaneous to "1_Hallsensor_manual").

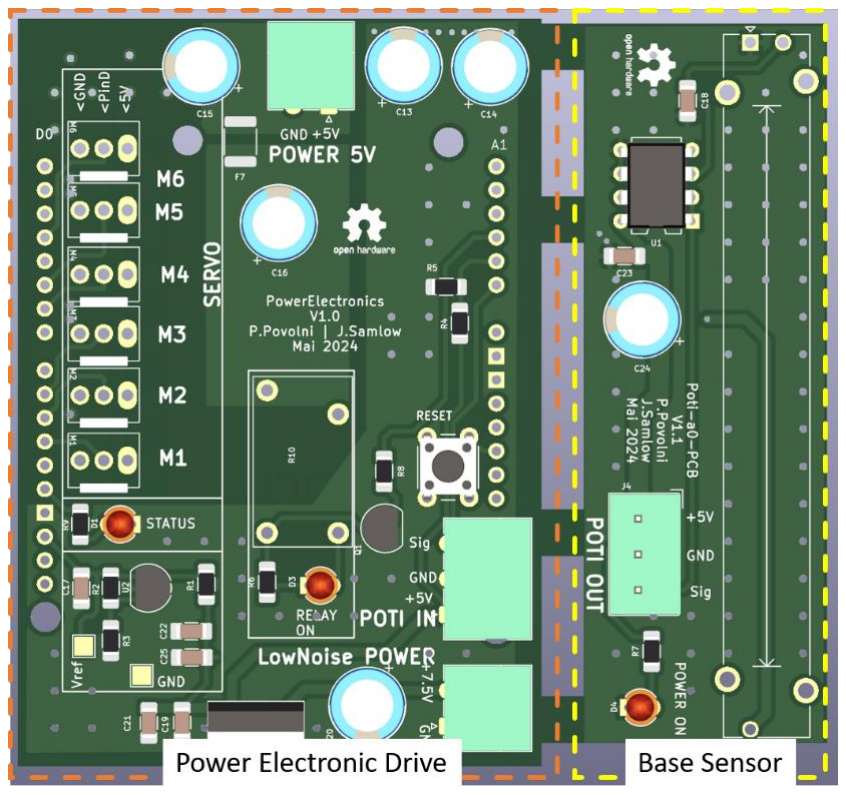
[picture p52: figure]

Figure 7 : Common PCB of the Power Electronic and the Base Sensor

3.1 Power Electronic Driver

This PCB is designed as a shield for an Arduino Uno. The Arduino is the controller of the robot (controls the motors, reads the base sensor) and communicates with the central PC on which the measurement is carried out.
This solves a central problem of the Braccio robot: During the boot time of the Arduino, the servo motors vibrate and shake very strongly and destroy the motor mount. Relay R10 therefore disconnects the power supply to the motors during the boot time and only switches it on when the system is in stable operating point.

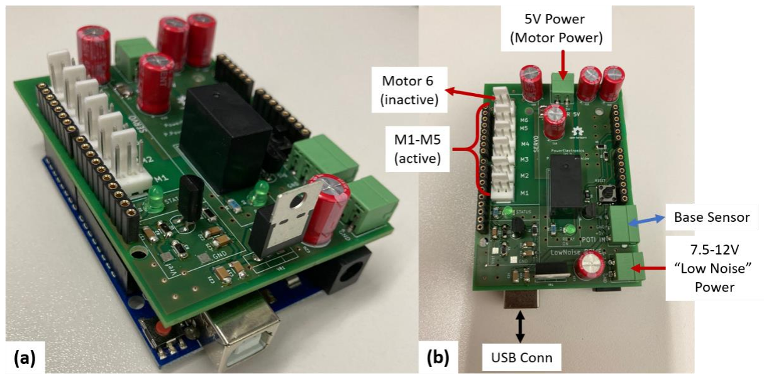
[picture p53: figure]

Figure 8: Photos of the assembled PCB with wiring

Soldering the PCB should not be a problem due to the large components used. There is only one special thing on the back that needs to be paid attention to (see Figure 9):

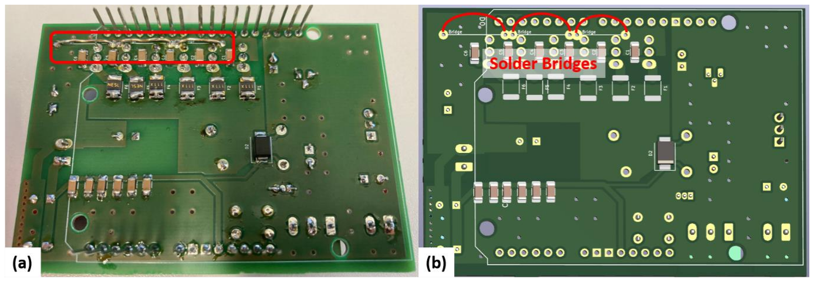
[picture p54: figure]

Figure 9: Solder Bridges on Backside of the PCB.

Two voltage sources are required:
1. One 5V | 4 A (voltage source for power electronics and motors)
2. One 7.5-12V | 0.5A "Low Noise" (voltage source for analog electronics). The noise
requirements are not particularly high. A normal laboratory power supply works perfectly

This PCB should also work for any other robot arm , which uses servo motors. In this case, it is best to test it with the motors loosely wired (not installed in the arm) to check everything.

The board is plugged onto an Arduino Uno. Any copy of the Arduino Uno (e.g. from Adafruit etc.) works the same way.

3.2 Base sensor

The base sensor PCB board is also very simple and can be soldered in just a few moments. Just make sure that the potentiometer is mounted on the correct side:

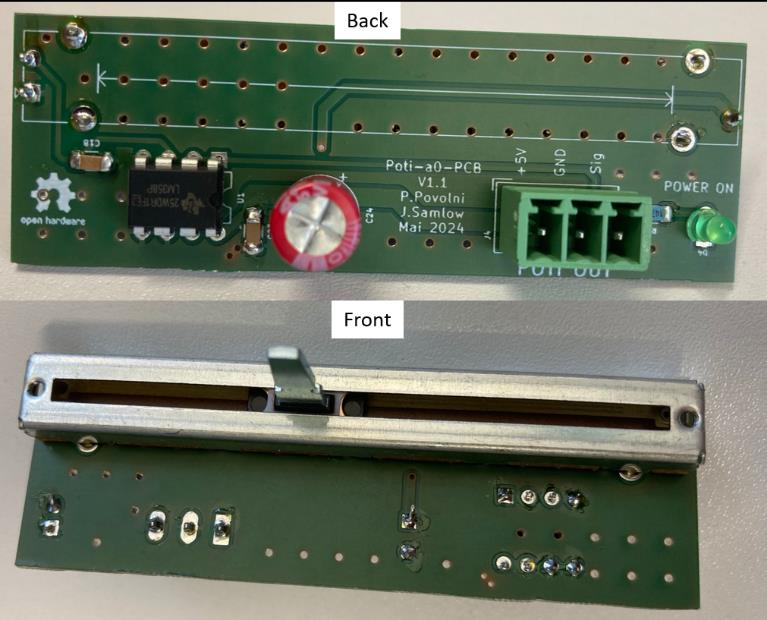
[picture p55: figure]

Figure 10: Front & Back of Base Sensor PCB

## 4 Embedded software

You can find the software here:
…\3_5DoF_Robot\32_Software\321_ArduinoCode

The script is optimized for the robot used. Presumably it works for other robot types in the same way, but only if servo motors are installed there. Other motors (e.g. stepper motors) cannot be controlled.

The software processes the commands received serially from the central computer and uses them to control the motors. In addition, the base sensor is read out and the measured angle is sent back to the computer.

What you need to change is commented in the software. Here are the most important parameters:
1. WRIST_ROTATION:
Set this rotation so that the Sensor Head is oriented as horizontally as possible. The value is then no longer changed in the measurement
2. Block StartUp position:
Moving the robot arm into the magnet in the center of the FOV is a very complicated trajectory and has to be simulated extensively (taking into account the mechanical tolerances) so that there is no crash and the sensor is not damaged. In the end, we decided to position the robot manually (motors de-energized) so that the sensor is already close to the center of the FOV. This means that the robot moves to the startup position is small. The startup position is approximately the center of the FOV (does not have to be exact). You can calculate the necessary angles using the scripts in the "4_Mapping_manual" manual, for example. These angles are saved in the parameters:
- alpha_Base | alpha_Shoulder | alpha_Ellbow | alpha_Wrist
3. alphaBase_Lin_a1 & alphaBase_Lin_a2:
Linearization factors from chapter 5.

4.1.1 Library
A self-written library is used for control: …\3_5DoF_Robot\32_Software\321_ArduinoCode\libs You must first install this in your environment. You can find the instructions here: https://docs.arduino.cc/retired/hacking/software/Libraries/4.1.2 Usage (Serial Commands)
Serial connection with 115200 baud.
To set the motors, the following example serial command is sent from the host PC:

+090,+120,+180,+060
In this case, the base is rotated to an angle of 90°, the shoulder to 120°, the elbow to 180° and the wrist to 60°.

The Arduino script only checks whether the motors are being operated within their mechanical limits. A crash with the magnet is not checked! Therefore, pay attention to which position is sent.

The base angle is averaged over 10 measurements. The serial response of the script after the robot has moved is:

...Braccio Angle. Base = 85.61| Shoulder = +120| Elbow = +180| Wrist = +60

Where the base angle is the measured value (2 decimal places). The other angles correspond to the angles from the command of the host PC.

## 5 Calibration of Base Sensor

An accurate measurement of the base sensor angle is essential for to get the full potential of the Motion Tracking and to produce a good mapping result.
There are 2 possibilities:
1. Very precise measurement of the mechanical lengths of the potentiometer and precise assembly of the PCB-part to the robot
2. Calibration of the sensor

Option 1 is difficult (we tried, but were not satisfied), so we ended up using option 2

5.1.1 SetUp
For the calibration, we provisionally attached a 3D rotation laser (self-leveling deactivated) to the robot (see Figure 11). Alternatively, an usual laser point can be used and mounted to the robot. A piece of DinA3 paper is attached at a distance of 60 cm on which the laser beams are projected and the position is marked (see Figure 11b).

The robot controller (see Ch. 4) is programmed with a new Arduino script that makes calibration easier ("Arduino_Robot_CheckAlpha0_withPoti.ino"). The script is similar to the original script. Only the base angle is changed during the measurement. It is programmed in such a way that 10 measuring points in both directions are carried out from a starting point in 1° steps.
Alternatively (as done in our case), the motors can be de-energized (5V supply switched off) and the robot can be turned by hand.
It is important that the base angle set in step 1 (first line) is 0°. The distances of the other measurements are then measured relative to this line.

The measuring sequence is as follows (in our case with de-energized motors):
1. Start Arduino, open a serial window on the PC (Arduino or Putty or Hterm or similar). Baud rate 115200 Bd
2. Move base to 0° position
3. Send a command serially on the PC (text doesn’t matter) – this starts the measurement
4. The Arduino measures the base sensor 10 times and outputs raw values serially. We are interested in the part "uout_x = 2.1225V(Raw..."
5. Mark the laser beam on the paper
6. Rotates the base to the next position
7. Continue with point 3 until measurement is complete. We have approached a total of 10 positions
You can either save the serial window and average the voltage measurements for each point afterwards. Or you can calculate the average during the measurement itself. In addition, the horizontal laser beam is marked on the paper (see next chapter).

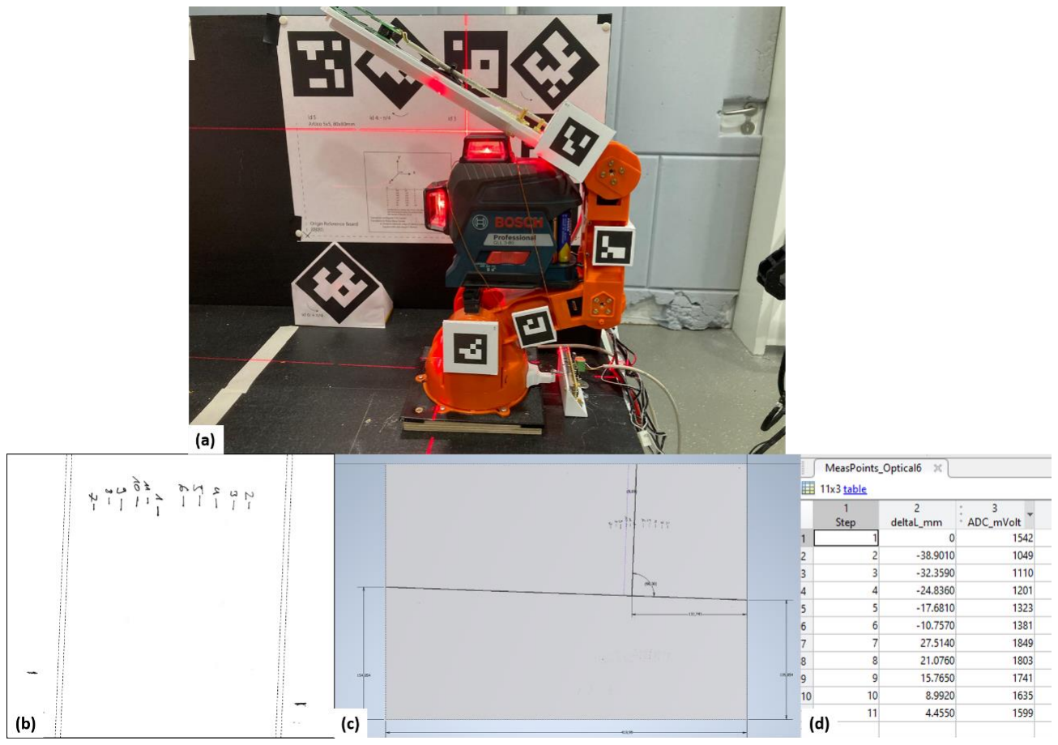
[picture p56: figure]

Figure 11: Setup for calibrating the base sensor. (a) Mounted 3D laser (b) Scan of the DinA3 sheet on which the laser projection was marked at the different base angles (the scan was scaled down here in the picture). (c)/(d) The image imported into CAD and measured.

5.1.2 Evaluation / Linearization
For linearization, the marked laser projection must be evaluated and the distance between the points measured.

This can be done simply by scanning the sheet and importing it into a CAD program. There, the distance between the markings and point 1 is measured (see Figure 11c). Make sure that the sign is correct:

- e.g. point 2 means a negative base angle
- The measured voltage decreases due to the potentiometer lever
- The sign of the distance is therefore negative

The measured markers and ADC voltages are combined in a table (in Matlab, Figure 11d).

The Matlab script "Evaluation_ArduinoLog.m" can be used to calculate the linear relationship from the measured values.

This will automatically calculate the linearization coefficients that are used during the mapping in the Arduino script (see Ch 4).

## 6 Power Supply

The robot is supplied with 2 voltage levels:
- 5V|5A, which are used to supply the motors.
- 7...25V|0.5A for the supply of the analog electronics (which are reduced to 5V on the PCB from chapter 3.1 with a “low-noise” L7805 voltage regulator)

In the simplest case, 2 adjustable laboratory power supplies are used for the power supply (in our case). However, fixed voltage sources can also be used without any problems.

The setup is sensitive to power cuts, as the motors in the robot are constantly running and powered. If the voltage drops briefly, the robot arm collapses and could damage the mounted sensor, for example.
If you want to use this setup in an area where the power supply is not guaranteed (e.g. at exhibitions, outdoor, or in areas with an unreliable grid), operation with a battery is possible without any problems. One possible solution is described here:

6.1 Power Supply Using conventional 12V Lead-Acid-Battery

For an exhibition, our setup was operated without access to a power socket.
The designed battery driven power supply is shown schematically in Figure 12. The circuit was built into a casing (see Figure 13 and Figure 14).

Essentially, the setup consists of a 12V battery (e.g. from UPS, motorcycles, cars, RC etc.), a battery guard (protection against deep discharge) and a 5V DCDC. A simple voltmeter was also added to see the charge level.
The used parts used are listed in Table 1.
The 5V|5A input of the robot is connected to the DIN connector (any other connector will do as well). The 7...12V input is connected directly to the Charge input (to the 4mm banana plugs).

Experience has shown that the robot requires a current of between 400-700mA (depending on position and weight) to hold the position. Theoretically, this can be up to 5A for a short time during movement (limited by the fuses on the power electronics board).
Assuming an average current consumption of 1.5A and a measurement duration of 180 minutes, this results in a energy requirement of 22.5Wh. Assuming a (very poor) efficiency of the DCDC of 80%, this results in 28.1W. Therefore, a lead battery (12V) with a capacity of 3Ah is completely sufficient for a 3h measurement (a 6Ah motorcycle battery is installed in the picture).

The batteries can be charged with a laboratory power supply unit via the “Charge input connectors”.

It is also possible to use the battery only as a buffer (quasi as a UPS):
A laboratory power supply unit is connected to the Charge input (14V, >2A, CC operation if necessary, diode in series to protect against backfeeding). This supply constantly charges the batteries. The robot is supplied via the battery guard and the DCDC.
If the grid power fails and the laboratory power supply unit switches off, the robot is supplied by the battery without any interruption.
The camera we use (see instructions “3_Motion_Tracking_manual”) has sufficient battery capacity for a 3h-mapping. It is advisable to use a camera with a USB charging input (power supply via power bank possible).
During mapping (see instructions “4_Mapping_manual”), the computer does not have to calculate anything intensive. A battery-powered laptop should be able to do this without any problems.

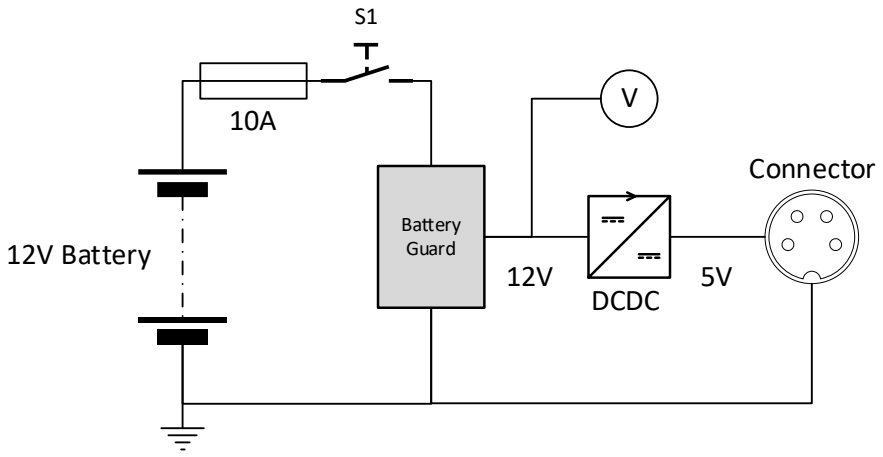
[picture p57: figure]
12V Battery; Battery Guard; DCDC; Connector

Figure 12: Schematic of the circuit

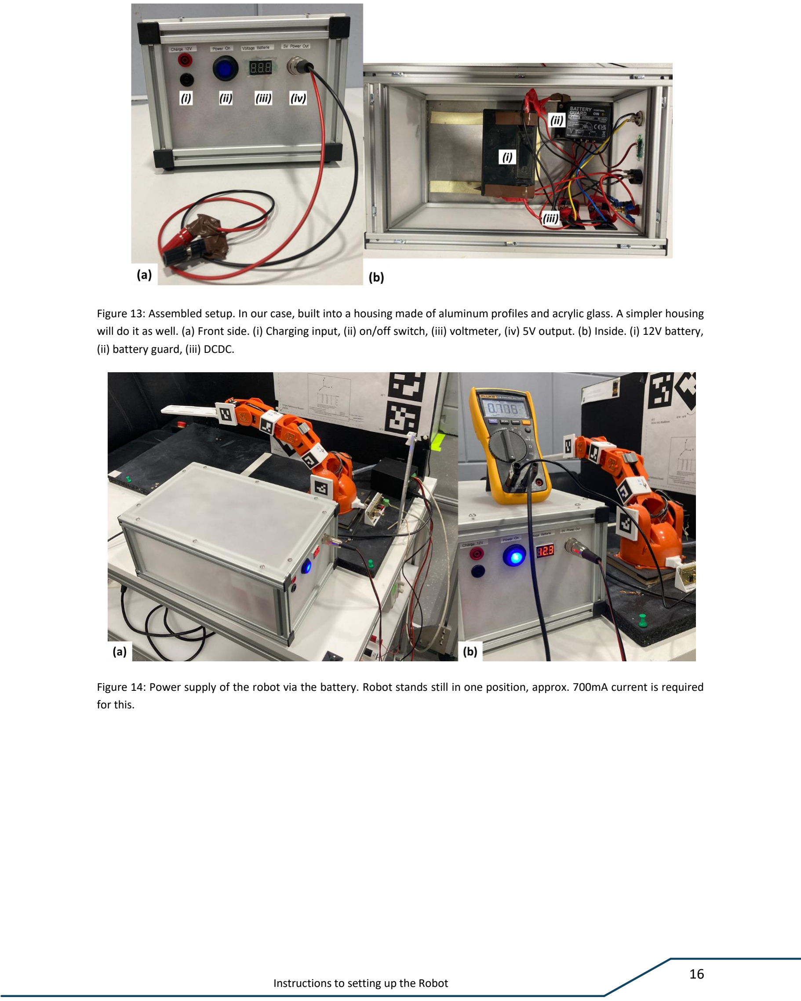
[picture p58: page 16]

Figure 13: Assembled setup. In our case, built into a housing made of aluminum profiles and acrylic glass. A simpler housing will do it as well. (a) Front side. (i) Charging input, (ii) on/off switch, (iii) voltmeter, (iv) 5V output. (b) Inside. (i) 12V battery, (ii) battery guard, (iii) DCDC.

Figure 14: Power supply of the robot via the battery. Robot stands still in one position, approx. 700mA current is required for this.

Table 1: Components used. The exact components are not critical and any other similar component can be used (especially the battery - just take what is available). The order number and link are from the shop Conrad Electronic SE from Germany.

Component | Description | Order Number * | Link*
Voltmeter | JOY-IT VM330 | 2435975 - 62 | Link (https://www.conrad.de/de/p/joy-it-messgeraet-2435975.html)
Battery Guard | Kemo Electronic M148A | 190095 - 62 | Link (https://www.conrad.de/de/p/kemo-m148a-batteriewaechter-12-v-dc-190095.html)
DCDC | JOY-IT SBC-Buck02 In 9-35V, Out 5V 5A | 2582436 - 62 | Link (https://www.conrad.de/de/p/joy-it-sbc-buck02-spannungsregler-1-st-2582436.html)
Connector (illuminated) | TRU COMPONENTS 1587920 | 1587920 - 62 | Link (https://www.conrad.de/de/p/tru-components-1587920-tc-r13-527d2b-druckschalter-14-v-dc-20-a-1-x-ein-aus-rastend-blau-1-st-1587920.html)
Banana connectors | TRU COMPONENTS 6239C26DN | 1565268 - 62 | Link (https://www.conrad.de/de/p/tru-components-6239c26dn-sicherheits-laborbuchse-buchse-einbau-vertikal-stift-o-4-mm-rot-1-st-1565268.html)
Battery 12V | Yuasa YTB9 | 3134958 - 62 | Link (https://www.conrad.de/de/p/yuasa-ytb9-motorradbatterie-12-v-9-ah-3134958.html)

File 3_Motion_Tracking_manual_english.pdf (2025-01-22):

## Instructions to setting up the

# Motion Tracking

Project

Easy Scalable, Low-Cost Open Source Magnetic Field Detection System for Evaluating Low-Field MRI Magnets using a Motion Tracked Robot

Pavel Povolni

October 2024

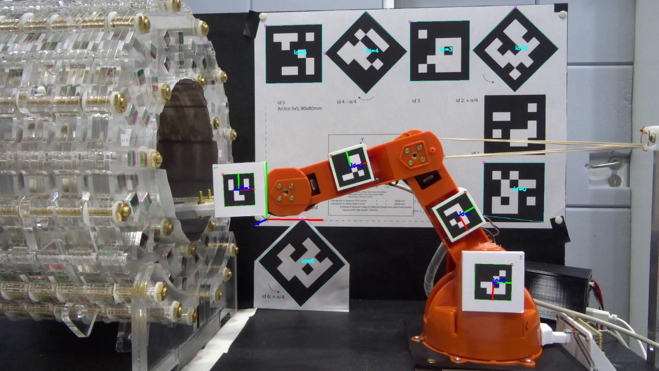
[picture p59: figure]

Instructions to setting up the Motion Tracking

## Content

1 | Preamble | 3
2 | Hardware | 3
2.1 | ArUco Marker | 3
2.1.1 | Reference Board | 3
2.1.2 | Robot Marker | 5
2.2 | Checkered Board for Calibration | 5
2.3 | Assembly of the reference board / distances from one another | 5
2.4 | Setup Camera | 5
3 | Calibration | 7
3.1 | Video Recording | 7
3.2 | Calibration in Post Processing | 7
3.2.1 | Check the structure | 8
3.2.2 | Preparation | 9
3.2.3 | Calibration | 10
4 | Motion Tracking during Mapping | 10
4.1 | Video Recording | 10
4.1.1 | During Measurement | 10
4.1.2 | Prepare Video Files for following Motion Tracking | 11
4.2 | Analysis in Post Processing | 12
4.2.1 | Preparation Software: Update SetUp File | 13
4.2.2 | Adapt Experiment Parameter | 14
4.2.3 | Run Analysis | 15
5 | Outlook | 15

## 1 Preamble

These instructions describe the Motion Tracking of the robot.
Further information can be found in the publication, as well as in the Appendix and Supplementary Information referenced there.
Software used:
- Motion Tracking: Python 3.9 and openCV 4.5.5
- Mechanical design (CAD): Autodesk Inventor 2022 (Commercial). All parts exported as .Steps
- Video Cutting Program: Vegas Pro 14 (any other free tool can also be used, e.g. OpenShot)

If you have any further questions, please contact us!

## 2 Hardware

The ArUco markers, which are then automatically detected by the software, are essential for Motion Tracking.

2.1 ArUco Marker

You can find the ArUco markers used at
...\4_MotionTracking\41_Hardware\411_ArUcoCodes

In principle, there is nothing to stop you from generating new ArUco markers or installing additional markers (e.g. to increase accuracy). You can generate ArUco markers using the openCV library in Python. For us it was more practical to generate the markers using this tool: https://chev.me/arucogen/
and to arrange the exported svg files that can be downloaded there in a image-program (e.g. Inkscape).

2.1.1 Reference Board
The reference board consists of 2 parts (the 2 PDF files in the folder ...\Reference Board).
The board "Reference_Board_Final.pdf" (part1) is printed out on normal DinA3-paper. Make sure that the file is not scaled. This document is glued to the back of the Reference System (see 2_Robot_manual/Chapter 2.4).
The paper is aligned with the edges of the Reference System (see Figure 1).

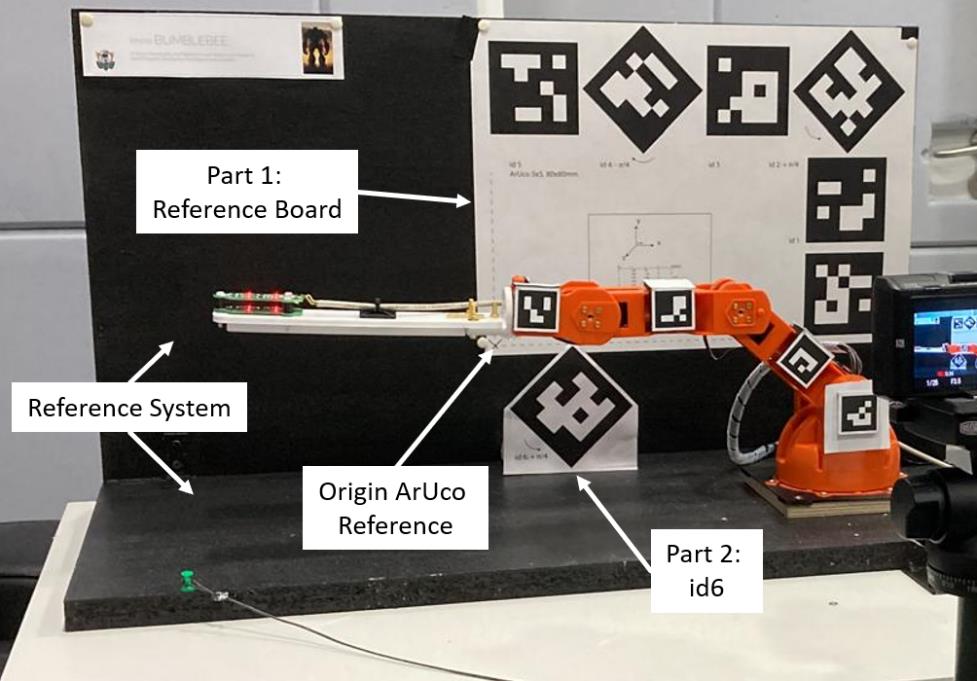
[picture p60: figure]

Figure 1: Setup of the environment + mounting of the reference board

The second part is the marker id6 (“Reference_Board_Final_id6.pdf”). A printout on DinA4 is sufficient here and you cut it out at the markings. This marker is mounted on an additional holder so that the Motion Tracking is more precise thanks to this additional depth information.
This holder consists of 2 parts (see Figure 2), both of which are 3D printed. Part 2 is firmly screwed into the Reference System, where it is touching the rear part of the Reference System. The horizontal position is determined using the auxiliary part. The support is aligned with the edge of the DinA3 sheet. This precise positioning is very important because this positioning is stored in the Motion Tracking evaluation.


Figure 2Mounting id6

2.1.2 Robot Marker
The Robot Markers are arranged on a sheet of A4 paper. After printing (normal paper), the markers are cut out at the markings and attached to the additional holders on the robot (see Ch 2.2, 2_Robot_manual.pdf).
Our holders are 3D printed from PETG. We have had good experiences with the glue "UHU stic". (https://www.uhu.com/en-en/products/uhu-stic-solvent-free-tray-21-g-multi-languag) Any other similar glue should work the same way.

2.2 Checkered Board for Calibration

You can find more details on the calibration itself in Ch 3.
A known chessboard pattern is required for calibration. The checkerboard pattern (9x13 boxes, 30x30mm) is available in
...\4_MotionTracking\41_Hardware\412_CheckeredBoard

Print out the board on a DinA3 sheet (no scaling) and glue it on a solid surface (e.g. on a wooden board or a plastic plate) so that it cannot bend.

2.3 Assembly of the reference board / distances from one another

see details in chapter 2.4 in Robot_manual.pdf

2.4 Setup Camera

We used a Sony HX60 as our camera (aperture f3.5). The optical & digital zoom were set to minimum, so the optical distortions are minimal. Any other comparable digital camera can be used in exactly the same way. It doesn't have to be an expensive one. The main thing is that it runs reliably during the measurement.
We carried out the Motion Tracking in post processing. The entire video was therefore saved on the SD card and only processed afterwards. In principle, Motion Tracking can also be reprogrammed so that the camera is read out live via USB. A camera that supports this is therefore recommended, but can be really expensive if it’s an “industrial one”.
An interface between OpenCV and the project libgphoto2 (through the API “VideoCaptureAPI” using CAP_GPHOTO2) (https://docs.opencv.org/4.5.5/d4/d15/group__videoio__flags__base.html) should to be possible, whereby libgphoto2 supports a variety of cameras using the PTP or MTP protocol: http://www.gphoto.org/proj/libgphoto2/support.php
(This interface was not tested, we used the webcam Logitech C920s for experiments with live connection or post processing in the presented experiment).

The camera was positioned in such a way that all markers covered as much of the image plane as possible (see Figure 3). The camera axis should be approximately in the middle (blue line) of the setup so that the inevitable distortions (caused by the imperfect camera optics) are evenly distributed or minimized.


Figure 3: Camera Setup

The camera should not be moved after calibration (see next chapter). To ensure this, we have connected the tripod to the Reference System using cords. This allows us to ensure that the camera is reliably stable during the measurement.
However, this connection was not stable enough for experiments on different days (the laboratory is used by several groups). The calibration process is automated as much as possible so that the distortion factors can be calculated quickly after a new calibration the next day.
In a follow-up development, it would make sense to design a camera holder that is permanently connected to the Reference System.

The camera was operated in FullHD mode at 25fps. Higher fps are not necessary (as the measurements are static). A higher resolution would be good for higher accuracy, but also means higher data volumes and therefore longer post processing.
Further information on calibration are given in the following chapter.

## 3 Calibration

Motion Tracking uses a camera that is inevitably not perfect. The camera optics therefore distort the image (e.g. fisheye effect etc.). If this distortion is known, the recorded image can be corrected, which significantly improves the accuracy of Motion Tracking itself.
You can find good instructions and an explanation of the calculation in the OpenCV tutorial: https://docs.opencv.org/4.x/dc/dbb/tutorial_py_calibration.html

The basic calibration procedure is as follows: The camera is fixed, a video with the checkered board is recorded, which is then processed using Python scripts (using openCV) and the distortion factors are calculated.

3.1 Video Recording

We have removed the magnet from the Reference System in order to fill as large an area of the camera as possible with the Checkered Board.
For calibration, the Checkered Board is swiveled and moved in front of the camera (see Figure 4). Make sure that all boxes are in the picture at all times (and nothing is cut off) and that they are not covered by the robot.


Figure 4: Checkered Board for Calibration

A video length of approx. 30 seconds has proven to be good.
Our camera saves the video file in a Sony format. But the Python script expects an .mp4 format. Therefore, the camera file must be converted to mp4, e.g. using the Video Cut program. An example video is available at:
...\4_MotionTracking\42_Software\0_calibration\calibration_video.mp4

3.2 Calibration in Post Processing

The entire Motion Tracking is based on an evaluation of the video files using Python scripts and the free openCV library. It is extremely important that the correct software versions are installed, otherwise the scripts will not work. A Conda environment is recommended. The most important versions are openCV 4.5.5 and Python 3.9.18. Details can be found in the following folder (including the YML file for installing the correct versions):
...\4_MotionTracking\42_Software\Environment

The calibration software can be found here: ... \4_MotionTracking\42_Software\0_calibration

3.2.1 Check the structure
It makes sense to check the position of the camera shortly before calibration and mapping to ensure that all markers can be detected. It could be, for example, that the lighting in the lab is not sufficient for reliable detection (this was a problem for us), the position of the camera is poor, or the camera itself is not working reliably (aperture, focus, etc.).

Proceed as follows for this check:
- Everything is set up the way you want it for mapping
- Start the camera and record a short video of the Robot Marker and Reference Marker (10-15s is enough). Take care, that all Robot Makers are clearly visible and not covered by something.
- Convert the video to .mp4 format if the camera does not save it that way
- Start the script "3_Main_Help_Detect_RobotMarker_VideoFile.py". Before that, change the variable "video_file" to the location of your video
- The script now analyses the video frame by frame, tries to detect ArUco markers and displays all detected markers in an additional window (example see Figure 5).
- It is important that all Robot Markers are recognized. If only a single Robot Marker is missing, the mapping will no longer work. The majority of the Reference Board Markers should be recognized to increase accuracy. In the example frame, id0 is not recognized because the robot's rubber band blocks the view. This is fine, as the other 6 markers are sufficient to create the reference coordinate system. In our tests, up to 2 missing markers were still ok.


Figure 5: An exemplary frame. All Robot Markers are recognized, as are most of the Reference Markers. A detected ArUco marker is labeled with a coordinate system, frame and id number.

3.2.2 Preparation
Images are used in calibration. The recorded video is therefore split into individual photos and saved.
- Data handling
The calibration video is saved in the following folder with the name "calibration_video.mp4": ...\4_MotionTracking\42_Software\0_calibration

The extracted photos are saved in the following folder: ...\4_MotionTracking\42_Software\0_calibration\calibration_result\img_calibration
The splitting script deletes the entire contents of this folder and then saves the new images in this folder
- Split images
The script "0_images_extraction.py" loads the video and extracts the photos. You don't have to change anything in the script. Just start it.
Only the "num_img" parameter could be changed if necessary. This is used to set the number of exported images (in equidistant time points). The value "300" was quite good (trade off between duration of calibration and accuracy of calculation).

3.2.3 Calibration
The script "1_camera_calibration.py" evaluates the photos and calculates the calibration factors. The software is commented in case something needs to be changed. But actually you don't need any adjustments (if you use the same Checkered Board).

Simply start the software and wait until all images have been processed and the calibration factors have been calculated.
The calculated factors are saved in the "cam_dist.csv" and "cam_mtx.csv" files. In addition, the so-called "reprojection error" is calculated, which is a measure of the accuracy of the camera-based Motion Tracking. This error is only displayed in the console (and not saved). It is worth making a note of this error to evaluate your Motion Tracking.

## 4 Motion Tracking during Mapping

Motion Tracking is part of the mapping of the magnet. Details on the mapping itself (control of the robot and sensor, evaluation, etc.) are listed in the instructions "4_Mapping_manual". This section describes the Motion Tracking during the experiment, as well as the evaluation of the recorded images.

4.1 Video Recording

4.1.1 During Measurement
The camera records all of the robot's movements throughout the experiment. This caused problems with our camera:
Typical (amateur and medium professional) cameras have a 30 minute recording limit due to customs regulations: https://www.recordinglimits.com/faq/
Due to this problem, the mapping control stops shortly before reaching this time limit and asks the user to stop and restart the recording. If you are using a different camera or the customs regulations are different from ours, you can skip this stop/start.

There is also a maximum file size that a single video file can have. This again depends on your hardware and your SD card. In our case, the camera automatically started a new video file after approx. 17 minutes (30 minutes become 17+13 minutes).
In our case, the mapping takes about 3 hours, which results in 12 individual video files with different lengths (17min, 12min + leftovers).

Smartphones don’t have a 30min limit, but may be limited in remaining memory. In case you have a high quality webcam, you can use the free Software “OBS Studio” (https://obsproject.com/de) on your PC to record the video. In experiments we didn’t had a time limit with this setup.
If you are using DSLR cameras with high resolution (e.g. 4K) you may have problems with overheating. So, here you can use the implemented break to cool your camera.

4.1.2 Prepare Video Files for following Motion Tracking
A continuous video in a single file (mp4 format) is required for automated Motion Tracking.
We manually cut the individual video files into a single video in a cutting program (commercial) and rendered it as mp4 (length approx. 2h50min, size 20Gb). We have also had good experiences with shorter recordings using the free software OpenShot (www.openshot.org). During the 3h experiment, the software did not seem to be so stable, but this could also be due to our PC hardware. It is worth a try.
The two files resulting from the file size limit (in our case the 17min limit) can simply be attached directly to each other in the cut program and would not have to be cut. This results in 30min clips (6 in our case)

The 30-minute limit is more problematic (in the following we just use the term “30-minute” limit, which may come from any limit like overtemperature, memory etc. and may be any other time duration).

Manual control of the camera results in different offset durations for each video file at the beginning (movement of the robot does not start immediately when the camera restarts) and end (user does not switch the camera off immediately as soon as the script reports it).
The following precautions have been taken to simplify this: The mapping script always waits exactly 20 seconds until the next movement of the robot. The start of this time period is the moment at which a new position is sent to the robot (for details, see the next instructions).

With this knowledge, the 30-minute clips can be cut in such a way that they can then simply be joined together in the cutting program.

Step 1: Start of the 30min- SubClip
Typically, a few seconds elapse between the manual camera restart and the continuation of the mapping (in the mapping script, an "Enter" in the command window is sufficient).
The start of the robot's movement is sought in this time period. The last frame in which the robot has not yet moved becomes the new start of the SubClip (cut point 1).
Step 2: End of the 30min-SubClips
The mapping script reports whether the 30-minute limit has been reached shortly before the next robot position is moved, whereby the limit is restricted to 28 minutes to ensure that all positions are mapped reliably. If the limit is reached, the experiment pauses and the user is informed by a message in the command window and beep signals.
As the measurement runs completely automatically, it is not always necessary for the user to stop the camera directly with the pause. If the user is attentive and pays attention, it is easy to find the end of the SubClip (approx. end of video minus a few seconds). If this is not the case, the last few minutes of the SubClip must be searched for.
For the end, search for the last movement of the robot. Again, look for the last frame before the movement begins (see step 1). The end of the SubClip is exactly 20 seconds (500 frames at 25fps) later.

In our setup, the shoulder motor was relieved via a suspension to increase the positioning radius. This suspension had to be retensioned during the measurement. Since retensioning takes some time, it also makes sense to restart the camera during this time. The cutting of the subclip is analogous to the 30min limit
Render the video at the end with the following settings:
- no color grading
- FullHD (1920*1080px)
- 25fps, PAL
- mp4 format
- audio track can be deactivated
- rendering good/optimal (no quality reduction of the image)
- color space standard (image is converted into gray image in the analysis).
The bit rate was variable for us (average 12Mbit/s, maximum 18Mbit/s, standard setting of our cutting program). We do not investigated whether this is important. Depending on the performance of your PC hardware (especially CPU power) and the length of the experiment, rendering can take up to several hours.

To be honest, this step is tedious and time-consuming and should be better solved. If you want to continue Motion Tracking in post processing, it makes sense to automate this step and use a Python script based on the MoviePy library, for example:
https://pypi.org/project/moviepy/ If possible, the reboot of the camera should be automated so that the merging of the files can be made easier (e.g. control of the camera via USB, Powercycle or similar).

4.2 Analysis in Post Processing

After the video has been prepared, the evaluation of the Motion Tracking can be started using the main script "2_Main_ArUco_Detection_PostProcessing.py".

The math used here (4x4 affine transformations) (https://www.euclideanspace.com/maths/geometry/affine/matrix4x4/index.htm) is described in the paper and appendix. If there are any questions, please let us know and we can describe the math in a new version of this manual.

The script analyzes the video and detects the actual angles of the robot joints for each position. It also detects the base angle, although this is replaced by the sensor value in the later evaluation of the mapping. This software has been programmed in an object-oriented manner and is presented below. Details should become clear from the detailed comments.

4.2.1 Preparation Software: Update SetUp File
First of all, the parameters of the software must match your robot and setup. If your setup is identical to ours, you don't need to change anything.
However, if you use a different robot or change the ArUco markers (position, size, library used), you must adjust the Motion Tracking.
These parameters are all stored in the class definition in the "MotionTracking_Classes.py" file and can be adapted to your setup:
- Reference Board
Class "ReferenceBoard" (determination of the origin of the Reference System)
- ID_List: All IDs of the markers that are installed on the Refrence board.
- Marker_length: Side length of the ArUco markers used
- ArucoDict: Library from which the markers come (in our case 5x5)
Class “MarkerReferenceBoard" (definition of the marker itself)
- mkX_T: Translation of each individual marker relative to the origin of the Reference System (X=1/2/3/4/5/6)
- mkX_rot_angle: Rotation of each individual marker relative to the origin of the Reference System (X=1/2/3/4/5/6)
- Robot Marker
Class "Robot_ArucoMarker" (all markers that are mounted on the robot)
- ID_List: All IDs of the markers that are mounted on the robot.
- Marker_length: Side length of the ArUco markers used
- ArucoDict: Library from which the markers come (in our case 4x4) Class “MarkerOnRobot" (definition of the marker itself)
- No change necessary
- Robot kinematics
Class "Robot_Cybernetics" (mechanical description of the robot and the position of the markers on the robot)
- In Chapter 1.2.3 of "2_Robot_manual" it was described how the exact position of the markers on the robot can be determined. These values are required in this class, see Figure 6


Figure 6: Customizable parameters in the class "Robot_Cybernetics". The orange circles show the parameters that can be adapted to your robot

4.2.2 Adapt Experiment Parameter
After adapting the software to the setup and robot, the software still needs to know about the experiment that has been carried out.

The following parameters are adjusted in the "2_Main_ArUco_Detection_PostProcessing.py" script for this purpose:
- count_pos: Number of different positions that were approached during the experiment
- video_file: Storage location of the rendered video
- can_dist/cam_mtx: Correction factors that have been calculated in the camera calibration. The storage location corresponds to the same location in which the calibration scripts also store these tables. Make sure that these files also match the experiment itself (e.g. if you repeat the analysis later)
- Avg_Frames: Number of frames over which the position is to be averaged (normal average to increase accuracy). A value between 100 (=4s) and 200 (=8s) was good
- MT_Time_Move: Dead time in which the robot moves to the new position, stops and has swung out of any subsequent shaking. This time must be the same as in the mapping script
- MT_Time_Meas: Duration in which the sensor carries out its measurement. This duration is always guaranteed (see Ch 4.1.2). This time must be the same as in the mapping script

During the analysis, the result of the Motion Tracking is saved in a csv table in the “\2_Save_Folder” folder. Before you start the analysis, delete old contents of this folder (or rename it). Otherwise the new values of this table will be appended at the end.
For debugging, an image with drawn (detected & averaged ArUco markers) is saved in the "\3_Images_MotionTracking" folder. Nothing is overwritten. But it makes sense to clean up the folder before the analysis to keep an overview.

4.2.3 Run Analysis
Once | everything | has | been | set | up | and | prepared, | execute | the | script
"2_Main_ArUco_Detection_PostProcessing.py".

Motion Tracking then runs automatically. Depending on which PC hardware you use (hard disk/CPU) and how many frames are averaged, it will take a while until the script is finished. If you want the analysis to be faster (e.g. for debugging), you can reduce the number of frames averaged.
The progress is displayed in the console.

During the analysis, a frame is displayed on which the detected markers (averaged position) are plotted. This frame is also saved.
If you notice any errors (especially if the drawn marker does not match the "real" marker), the script should be aborted.
Problems we had at this point, which caused mispositioned ArUco marker in the detection:
- Lightning of the experiment too poor. Either increase the brightness of the video (e.g. in the cutting program), or repeat the experiment.
But before repeating it, use Chapter 3.2.1 and check the setup.
- The parameters “MT_Time_Move”/ ”MT_Time_Meas” did not matched the experiment, so that the roboter movement was part of the analysis and falsified the result.

## 5 Outlook

In our setup, Motion Tracking was carried out entirely in post-processing, which is quite time-consuming. However, this gives you complete control and makes debugging much easier.

A live analysis of the position during the mapping itself would be an advantage and should be easy to integrate. For that it is important to establish a connection to the camera via openCV (it worked for us with a FullHD webcam. However, the distortion of the image was horrible, so it made little sense).

A good integration of the Python scripts (used in Motion Tracking) into the Matlab scripts (used in the Mapping) should be checked.
We conducted our first experiments using a software localhost:
A localhost is opened in the Matlab script, to which the Python script connects via the "socket" library. The result of the Motion Tracking is then transferred via this line.

It would probably make more sense to translate the Matlab scripts into Python. This should not be a major problem as no special toolboxes are used.

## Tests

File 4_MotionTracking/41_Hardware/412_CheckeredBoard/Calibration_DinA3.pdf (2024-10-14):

Checkered Board for Camera Calibration. 30x30mm Squares. 9 x 13. MPI bioKyb, P. Povolni, 02/24

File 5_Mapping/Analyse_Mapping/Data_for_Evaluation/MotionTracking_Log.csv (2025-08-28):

FrameStart | FrameEnd | RefB_EulerZ | RefB_EulerY | RefB_EulerX | RefB_TvecX | RefB_TvecY | RefB_TvecZ | Robot_alpha0 | Robot_alpha1 | Robot_alpha2 | Robot_alpha3
250.0 | 350.0 | 0.0012456273584535715 | 0.012403172826641162 | -3.137548436154564 | -0.5816882245339253 | -0.21395502999245722 | 1.3315006714788198 | 0.3486220975123101 | 0.47927414482212144 | 1.3483497912016442 | -0.37717402033968805
750.0 | 850.0 | 0.0005719783448860927 | 0.012559551120331802 | -3.1368726259456032 | -0.5816205166931582 | -0.21413558642717825 | 1.3308616177604191 | 0.0683613526333692 | 0.48198790902777217 | 1.2996285980531794 | -0.17359259168851127
1250.0 | 1350.0 | 0.0007412452487434162 | 0.01638283443565358 | -3.1375697513733094 | -0.5822193920127451 | -0.21441202736524298 | 1.331857619869653 | 0.0905836929725484 | 0.44033816829583383 | 1.191171169806681 | -0.016397687786131335
1750.0 | 1850.0 | 0.0018273780253854621 | 0.016882179594817304 | -3.136293347961943 | -0.5820559418859041 | -0.21443323654937593 | 1.3324253771442842 | 0.03316919135152622 | 0.47274100627640236 | 1.1730999754672693 | -0.013259807884258144
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

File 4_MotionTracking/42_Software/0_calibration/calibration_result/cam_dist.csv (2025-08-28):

4.298837445271929542e-02 -1.540590669667118440e-01 2.685408242765792517e-03 -6.237450080785243798e-04 1.095606285226084081e-01

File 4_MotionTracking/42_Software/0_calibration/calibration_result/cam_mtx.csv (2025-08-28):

1.383960808315501708e+03 0.000000000000000000e+00 9.456929442049577119e+02
0.000000000000000000e+00 1.392650272861353415e+03 5.441954854511384383e+02
0.000000000000000000e+00 0.000000000000000000e+00 1.000000000000000000e+00

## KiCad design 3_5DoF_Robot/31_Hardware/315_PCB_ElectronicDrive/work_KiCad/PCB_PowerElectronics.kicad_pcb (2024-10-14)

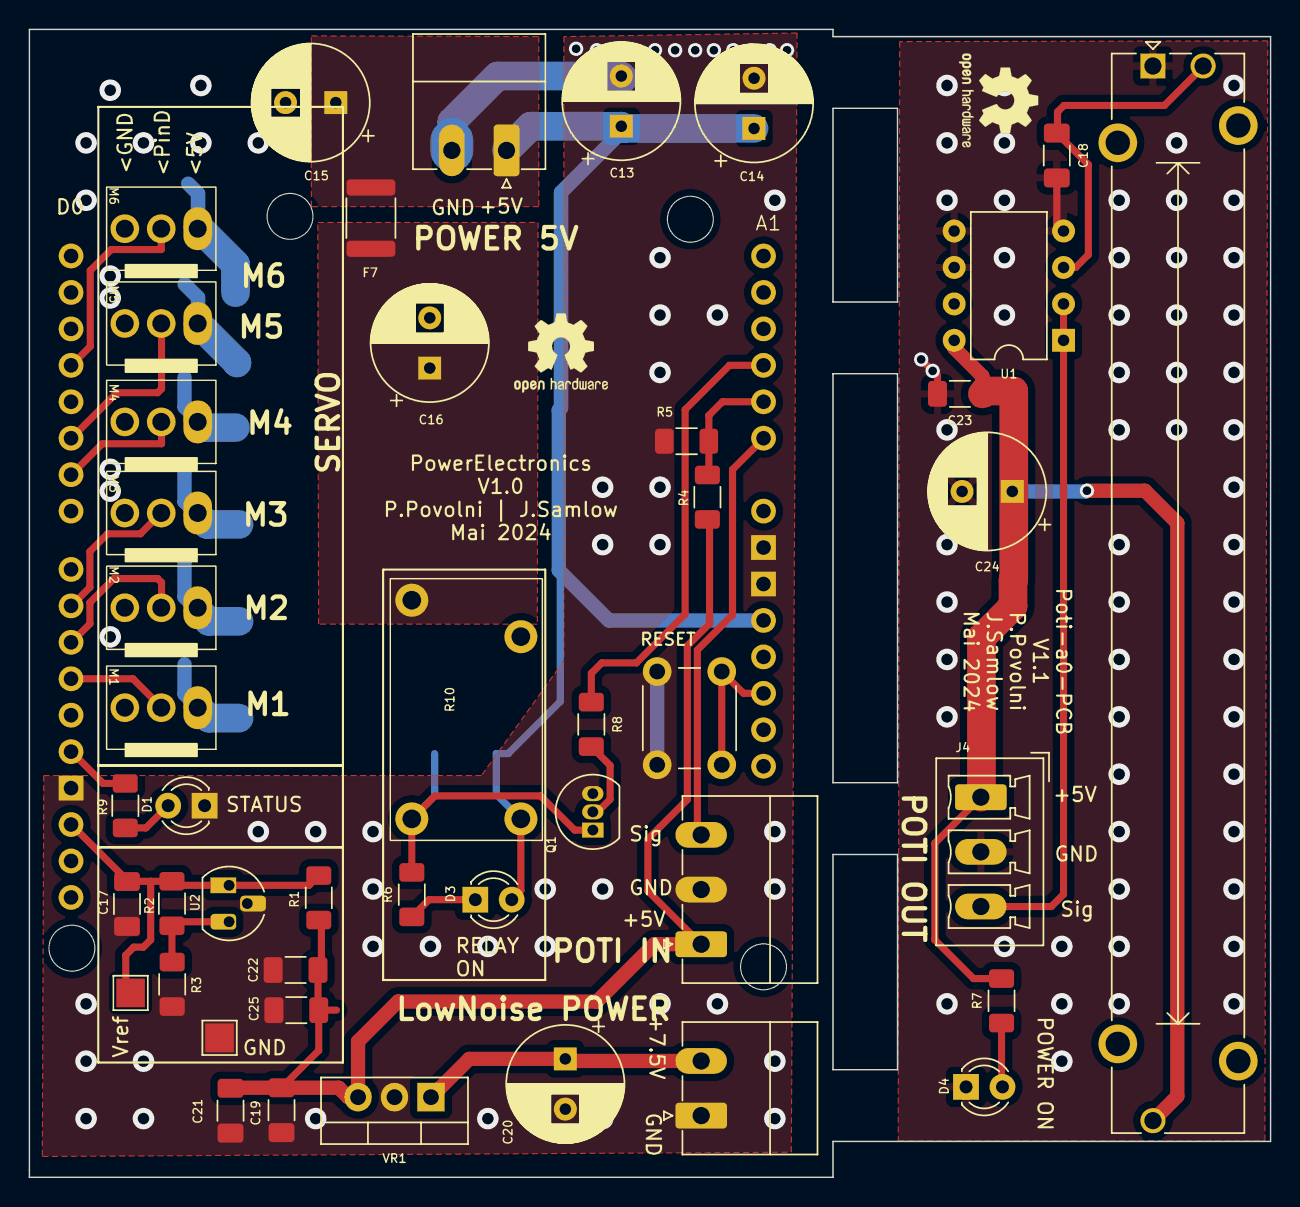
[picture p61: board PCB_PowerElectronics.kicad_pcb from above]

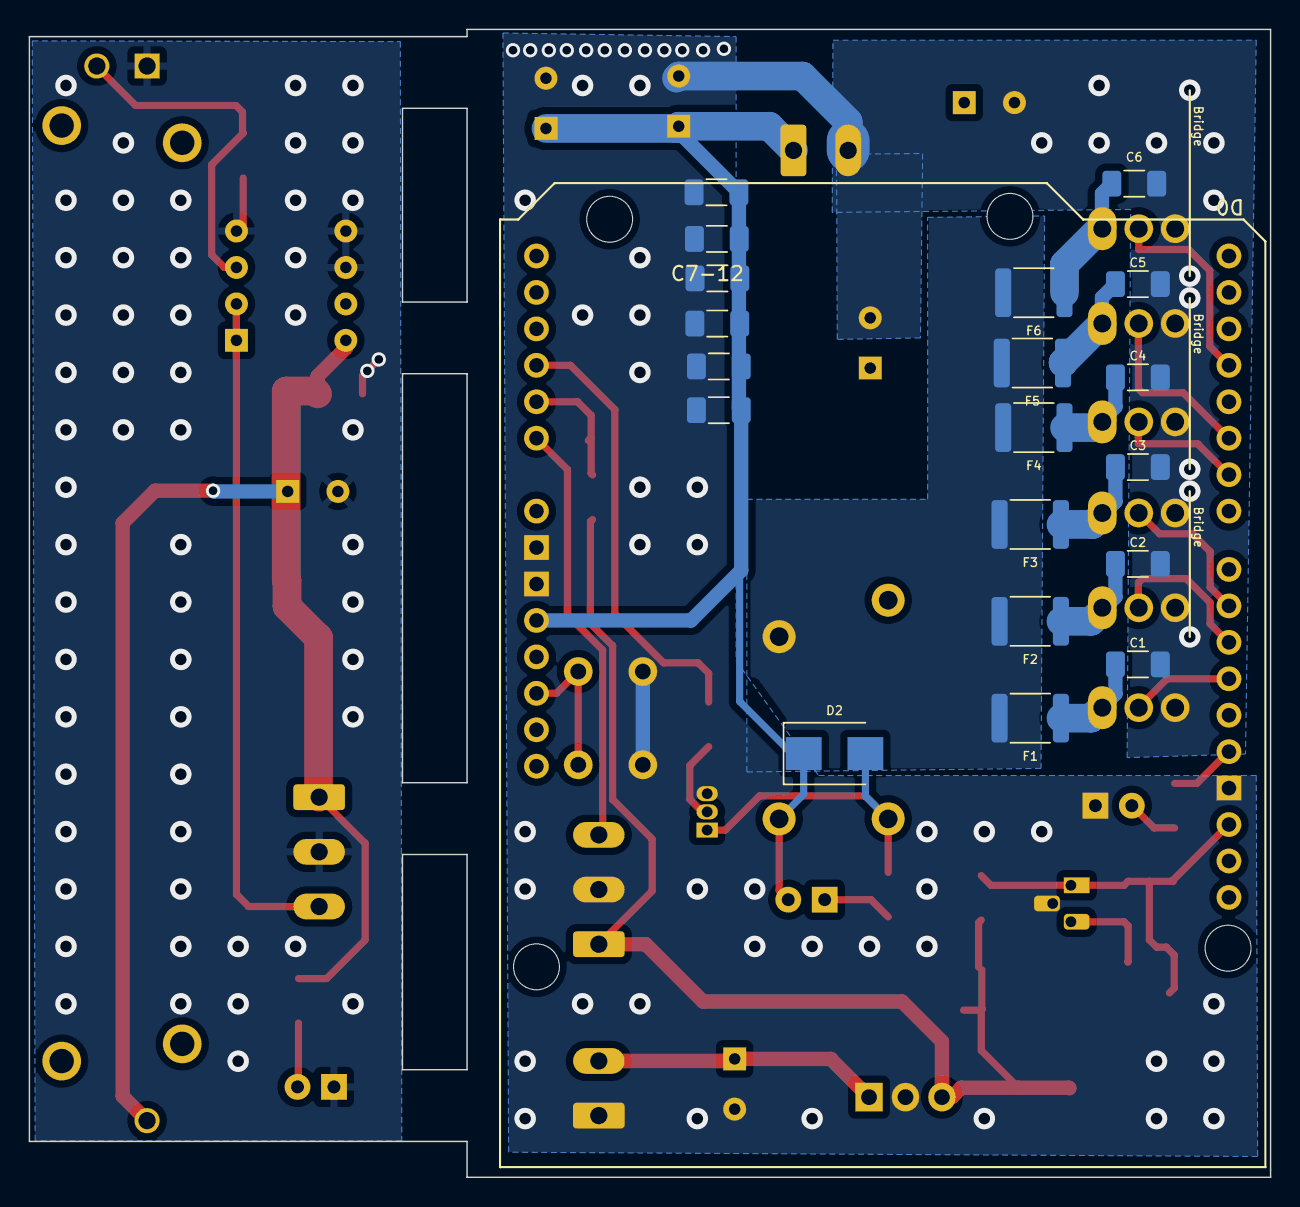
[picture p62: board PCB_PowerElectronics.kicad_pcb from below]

Board: 2 copper layers, 86.5 x 80.0 mm, 63 parts (19 on the bottom side), 32 nets.

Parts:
A1: Arduino_Uno; Arduino Uno Shield Mini BBB
C1, C2, C3, C4, C5, C6, C21, C25: 1µF; C_1206_3216Metric_Pad1.33x1.80mm_HandSolder
C7, C8, C9, C10, C11, C12: 100 n; C_1206_3216Metric_Pad1.33x1.80mm_HandSolder
C13, C15, C16: 47 µF; CP_Radial_D8.0mm_P3.50mm
C14, C20, C24: 47µF; CP_Radial_D8.0mm_P3.50mm
C17, C18, C19, C22, C23: 100n; C_1206_3216Metric_Pad1.33x1.80mm_HandSolder
D1: gelb; LED_D3.0mm
D2: S2A; D_SMB
D3: LED; LED_D3.0mm
D4: rot; LED_D3.0mm
F1: MF-MSMF 1100mA; Fuse_1812_4532Metric
F2, F3, F4: MF-MSMF 1100 mA; Fuse_1812_4532Metric
F5, F6, F7: MF-MSMF 750 mA; Fuse_1812_4532Metric
J1: 5V; PhoenixContact_MC_1,5_2-G-3.81_1x02_P3.81mm_Horizontal
J2: 7V; PhoenixContact_MC_1,5_2-G-3.81_1x02_P3.81mm_Horizontal
J3: Poti; PhoenixContact_MC_1,5_3-G-3.81_1x03_P3.81mm_Horizontal
J4: Poti; PhoenixContact_MCV_1,5_3-G-3.81_1x03_P3.81mm_Vertical
M1, M2, M3, M4, M5, M6: Molex_22272031; Molex_3Pin_Header
Q1: BC548A; TO-92_Inline
R1: 147, E192; R_1206_3216Metric_Pad1.30x1.75mm_HandSolder
R2: 1210, E192; R_1206_3216Metric_Pad1.30x1.75mm_HandSolder
R3, R4, R5: 2370, E192; R_1206_3216Metric_Pad1.30x1.75mm_HandSolder
R6, R7, R9: 147; R_1206_3216Metric_Pad1.30x1.75mm_HandSolder
R8: 1k; R_1206_3216Metric_Pad1.30x1.75mm_HandSolder
R10: Relay_AHQSH105LM100G
RV1: Poti; Potentiometer_Bourns_PTA6043_Single_Slide
SW1: RESET; SW_PUSH_6mm
U1: LM358; DIP-8_W7.62mm
U2: TL431C; TO-92_HandSolder
VR1: 7805; TO-220-3_Vertical

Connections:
+5V: A1.5V1 (5V), C7.1, C8.1, C9.1, C10.1, C11.1, C12.1, C13.1, C14.1, C15.1, D2.1 (K), D3.2 (A), F7.1, J1.1, R10.1
+5VA: C19.1, C21.1, C22.1, C23.1, C24.1, C25.1, J3.3, J4.1, R1.1, R4.1, R7.1, RV1.3, U1.8 (V+), VR1.3 (VO)
+5V/ Fused: C16.1, F7.2, R10.3
+5V/ Mot: F1.2, F2.2, F3.2, F4.2, F5.2, F6.2, R10.4
+7.5V: C20.1, J2.2, VR1.1 (VI)
/3,722 V (Aref): A1.AREF, C17.1, R1.2, R2.1, U2.3 (K)
/A0: A1.A0, J3.1
/A1: A1.A1, R4.2, R5.1
/A2: A1.A2, R8.1
/D3: A1.D3 (D3_INT1), M6.2
/D5: A1.D5, M5.2
/D6: A1.D6, M4.2
/D9: A1.D9, M3.2
/D10: A1.D10 (D10_CS), M2.2
/D11: A1.D11, M1.2
/D13: A1.D13, R9.1
/Poti/Pin A0: J4.3, U1.1, U1.2 (-)
GND: A1.GND1 (GND), A1.GND2 (GND), A1.GND3 (GND), C1.2, C2.2, C3.2, C4.2, C5.2, C6.2, C7.2, C8.2, C9.2, C10.2, C11.2, C12.2, C13.2, C14.2, C15.2, C16.2, C17.2, C18.2, C19.2, C20.2, C21.2, C22.2, C23.2, C24.2, C25.2, D1.1 (K), D4.1 (K), J1.2, J2.1, J3.2, J4.2, M1.3, M2.3, M3.3, M4.3, M5.3, M6.3, Q1.3 (E), R3.2, R5.2, RV1.1, SW1.2 (D), U1.4 (V-), U1.5 (+), U1.6 (-), U2.2 (A), VR1.2 (GND)
unnamed: A1.RST1 (RESET), SW1.1 (C)
unnamed: D1.2 (A), R9.2
unnamed: D2.2 (A), Q1.1 (C), R6.2, R10.2
unnamed: D3.1 (K), R6.1
unnamed: D4.2 (A), R7.2
unnamed: C1.1, F1.1, M1.1
unnamed: C2.1, F2.1, M2.1
unnamed: C3.1, F3.1, M3.1
unnamed: C4.1, F4.1, M4.1
unnamed: C5.1, F5.1, M5.1
unnamed: C6.1, F6.1, M6.1
unnamed: Q1.2 (B), R8.2
unnamed: C18.1, RV1.2, U1.3 (+)
unnamed: R2.2, R3.1, U2.1 (REF)

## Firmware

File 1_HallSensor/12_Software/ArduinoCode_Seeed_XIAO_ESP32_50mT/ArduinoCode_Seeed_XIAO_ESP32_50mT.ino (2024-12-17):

/**********************************************************************/
//     LOW FIELD HALL SENSOR - 8 Channel
//     
//    Using the Chip ALS31313 from Allegro Microsystems and ESP32 µC (Seeed XIAO)  
//    Parts of this Software (Readout of Hallsensor in Fast Mode) is based on Example Code from Allegro
//
//    One other good example is published here by vintlabs: https://github.com/vintlabs/ESP32-Arduino-3dHall-Example/tree/master
// 
//    Copyright (c) 2024 Pavel Povolni, Tuebingen, Germany
//    MIT LICENSED
//    Have fun guys!
/**********************************************************************/

// Define I2C Protocol
#include <Wire.h>
// #define SDA 4
// #define SCL 5

// Variables used I2C Transmit

#define kNOERROR 0
#define kDATATOOLONGERROR 1
#define kRECEIVEDNACKONADDRESSERROR 2
#define kRECEIVEDNACKONDATAERROR 3
#define kOTHERERROR 4


// I2C Baud Rate
const long i2cclock = 100000;  // Baud/Hz 

// LEDs
#define LED_H1 D0
#define LED_H2 D1
#define LED_H3 D2
#define LED_H4 D3
#define LED_H5 D6
#define LED_H6 D10
#define LED_H7 D9
#define LED_H8 D9 //  1 LED too few -> H7 and H8 share the LED
#define LED_Sts D8


// Hall Sensirs
#define Hall_Sensitivity_1000  2.0  // 1000 Gauss Type
#define Hall_Sensitivity_500  4.0   // 500  Gauss Type

const float Hall_Sensitivity = Hall_Sensitivity_500; // Here: 50mT Type

const int Address_H1 = 96;  // Hall 1
const int Address_H2 = 99;   // Hall 2
const int Address_H3 = 100;  // Hall 3
const int Address_H4 = 103;  // Hall 4
const int Address_H5 = 104;  // Hall 5
const int Address_H6 = 107;  // Hall 6
const int Address_H7 = 108;  // Hall 7
const int Address_H8 = 110;  // Hall 8

// Number of averaged measurements
const int Repeat_Steps = 1000; //Number of internal repetitions, these values are averaged arithmetically.

// Hall Mode: Single-Ended Operation, reports mag data from X/Y/Z
const int hall_mode = 0;  




// Serial Connection to Computer (USB)
const long baud_rate = 115200;
const int num_decimal = 6; //  Number of decimal places in the serial output

// Measure Data - Return Value 
int64_t xd = 0;
int64_t yd = 0;
int64_t zd = 0;
int64_t td = 0;

// Prototype Functions
String Hall_Read_Full_Loop(int,String);
uint16_t Hall_Read(int, uint8_t, uint32_t&);
uint16_t Hall_Write(int, uint8_t, uint32_t);
long SignExtendBitfield(uint32_t, int);
void setLED(int);
void Hall_Read_Single(int);
void Hall_SetCustomer_Access(int, String);

// Structure 1 Serialline
String Text_H1="";
String Text_H2="";
String Text_H3="";
String Text_H4="";
String Text_H5="";
String Text_H6="";
String Text_H7="";
String Text_H8="";
String Text_Total = "";

void setup() {

  // Start I2C
  Wire.begin(SDA, SCL);
  Wire.setClock(i2cclock);

  // Serial Communication with PC
  Serial.begin(baud_rate);
  while (!Serial){}
  delay(10); //  Wait 10ms to be on the safe side, so that the Hall sensor has started safely and is listening to commands


  // LED Pins as Output
  pinMode(LED_Sts, OUTPUT);
  pinMode(LED_H1, OUTPUT);
  pinMode(LED_H2, OUTPUT);
  pinMode(LED_H3, OUTPUT);
  pinMode(LED_H4, OUTPUT);
  pinMode(LED_H5, OUTPUT);
  pinMode(LED_H6, OUTPUT);
  pinMode(LED_H7, OUTPUT);
  

  // Set Customer Write Access on ALS31300 (p20 Datasheet)
  Hall_SetCustomer_Access(Address_H1, "Hall 1");
  Hall_SetCustomer_Access(Address_H2, "Hall 2");
  Hall_SetCustomer_Access(Address_H3, "Hall 3");
  Hall_SetCustomer_Access(Address_H4, "Hall 4");
  Hall_SetCustomer_Access(Address_H5, "Hall 5");
  Hall_SetCustomer_Access(Address_H6, "Hall 6");
  Hall_SetCustomer_Access(Address_H7, "Hall 7");
  Hall_SetCustomer_Access(Address_H8, "Hall 8");


  
}

void loop() {

    bool succ = false;

    // Readout Hall 1
    setLED(LED_H1);
    //Serial.print("H1;   ");
    Text_H1 = Hall_Read_Full_Loop(Address_H1,"H1");  // Data is stored in xd,yd,zd,td
    setLED(LED_H1);
    // Readout Hall 2
    setLED(LED_H2);
    //Serial.print("H2;   ");
    Text_H2 = Hall_Read_Full_Loop(Address_H2,"H2");  // Data is stored in xd,yd,zd,td
    setLED(LED_H2);
    // Readout Hall 3
    setLED(LED_H3);
    //Serial.print("H3;   ");
    Text_H3 = Hall_Read_Full_Loop(Address_H3,"H3");  // Data is stored in xd,yd,zd,td
    setLED(LED_H3);
    // Readout Hall 4
    setLED(LED_H4);
    //Serial.print("H4;   ");
    Text_H4 = Hall_Read_Full_Loop(Address_H4,"H4");  // Data is stored in xd,yd,zd,td
    setLED(LED_H4);
    // Readout Hall 5
    setLED(LED_H5);
    //Serial.print("H5;   ");
    Text_H5 = Hall_Read_Full_Loop(Address_H5,"H5");  // Data is stored in xd,yd,zd,td
    setLED(LED_H5);
    // Readout Hall 6
    setLED(LED_H6);
    //Serial.print("H6;   ");
    Text_H6 = Hall_Read_Full_Loop(Address_H6,"H6");  // Data is stored in xd,yd,zd,td
    setLED(LED_H6);
    // Readout Hall 7
    setLED(LED_H7);
    //Serial.print("H7;   ");
    Text_H7 = Hall_Read_Full_Loop(Address_H7,"H7");  // Data is stored in xd,yd,zd,td
    setLED(LED_H7);
    //Readout Hall 8
    setLED(LED_H8);
    //Serial.print("H8;   ");
    Text_H8 = Hall_Read_Full_Loop(Address_H8,"H8");  // Data is stored in xd,yd,zd,td
    setLED(LED_H8);

    //Send Data via UART
    setLED(LED_Sts);
    Text_Total = Text_H1 + "|" + Text_H2 + "|" + Text_H3+ "|" + Text_H4+ "|" + Text_H5+ "|" + Text_H6+ "|" + Text_H7+ "|" + Text_H8;
    Serial.println(Text_Total);
    setLED(LED_Sts);   
   
}

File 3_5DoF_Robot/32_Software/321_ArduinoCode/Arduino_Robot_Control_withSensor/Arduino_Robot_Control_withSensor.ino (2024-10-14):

/**********************************************************************/
//    ARDUINO_ROBOT_CONTROL_WITHSENSOR to control the 5DoF robotic arm
//     
//    Here the Robotic Arm "TinkerCAD Braccio" was used with a self-developed Driver Shield
//
//    In order to improve the performance a self developed Library "BraccioV2slowed" was used
//    which is based on the published library "BraccioV2" from Lukas Severinghaus:
//      * https://www.arduino.cc/reference/en/libraries/bracciov2/
//      * https://github.com/kk6axq/BraccioV2
//    (Licensed under GNU GPL v3 license)
//
//    Copyright (c) 2024 Pavel Povolni, Tuebingen, Germany
//    MIT LICENSED
//    Have fun guys!
/**********************************************************************/

// 1) INCLUDE & DEFINES

// Defining Robotic Arm related objects/variables
#include <Servo.h>            // standard Arduino library (can be installed through lib manager)
#include "BraccioV2slowed.h"  // new library (see libs folder in github)
#define GRIPPER_POS 78        // The Braccio has a gripper (6th DOF), which is not connected in our system -> use the standard value here
#define WRIST_ROTATION 74     // The Wrist rot angle is set once during the setup to adjust the rotation as horizontal as possible. Then its kept constant

// Used Pins on Power Drive Shield 
#define RELAIS_POWER 14       // Relais Switch on/off
#define STS_LED 13            // Status LED

// 2) Generate Objects
Servo base;
Servo shoulder;
Servo elbow;
Servo wrist_rot;
Servo wrist_ver;
Servo gripper;

Braccio arm;

// 3) Define used variables
bool update = false;
String readString = "";

// min/max angle (Degree) for every jpint - determined during setup 
int base_min = 0;
int base_max = 180;
int shoulder_min = 14;
int shoulder_max = 166;
int ellbow_min = 0;
int ellbow_max = 180;
int wrist_min = 0;
int wrist_max = 180;

// StartUp-Position: Must be found before measurements. Sensor should be postioned already inside the Magnet
// During the startup the servo motors are not powered (Relais disconnects the power)
// Then after powering the sensor will be moved fast into the start position. Therefore the sensor should be already inside the magnet near the start position
// It has proven useful to manually hold the sensor close to its starting position when powering the Arduino until the motors are powered (approx 10sec)   
int alpha_Base = 85;
int alpha_Shoulder = 45;
int alpha_Ellbow = 55;
int alpha_Wrist = 70;

// Calibration Angles, in case motors have some tolerances. 
// Here: Better use standard values (90°). Set the tolerances directly in your Control Software (ie Matlab/Python Script)
int alpha_Base_cal = 90;
int alpha_Shoulder_cal = 90;
int alpha_Ellbow_cal = 90;
int alpha_Wrist_cal = 90;

// Readout of Angle of Potentiometer (extra Base Angle Sensor)
int PotiPin = A2;
int UccPin = A1;
double Uref_ADC = 3.745;    //V, set to your Reference Voltage on your design
double lpoti = 56.5;        //mm, Properties of sensor system 
double Ucc = 5.0;           //V
double l = 77.698;          //mm
double x0 = 18.96;          //mm
double alphaBase_Lin_a1 = 7.633209009676445; //°/V calcualted with calibration/linearization + Smallangle Approx, alphaBase = a1*Volt+a2 in °
double alphaBase_Lin_a2 = -11.672975576939738 ; //° calc with calibration/Linearization


double k ; 
int uout_x_raw;
double uout_x;
double x;
double x_s; 
double alpha_meas_rad;
double alpha_meas; 
double alpha_Base_meas;
String alpha_Base_meas_Str;



// 4) SETUP THE ARDUINO
void setup() {

  analogReference(EXTERNAL);  // Set External Reference Voltage (Uref_ADC)

  // Using Pin A0 = D14 as Relais-Bridge to disconnect the power to the Power-Shield to prevent the robot from jumping around during StartUp
  pinMode(RELAIS_POWER,OUTPUT);
  // Using Pin D13 as a Status LED on the Power-shield
  pinMode(STS_LED,OUTPUT); 
 
  digitalWrite(RELAIS_POWER,LOW); // Relais is off -> No Power is sent to the Power-Shield
  digitalWrite(STS_LED,LOW);


  Serial.begin(115200);
  Serial.println("Initializing... Please Wait");  //Start of initialization

  //Update these lines with the calibration angles
  arm.setJointCenter(BASE_ROT, alpha_Base_cal);
  arm.setJointCenter(SHOULDER, alpha_Shoulder_cal);
  arm.setJointCenter(ELBOW, alpha_Ellbow_cal);
  arm.setJointCenter(WRIST, alpha_Wrist_cal);
  arm.setJointCenter(WRIST_ROT, WRIST_ROTATION);
  arm.setJointCenter(GRIPPER, GRIPPER_POS);

  arm.setDelta(BASE_ROT,1);
  arm.setDelta(SHOULDER,1);
  arm.setDelta(ELBOW,1);
  arm.setDelta(WRIST,1);
  arm.setDelta(WRIST_ROT,1);
  arm.setDelta(GRIPPER,1);

 //Start to custom position.
  arm.begin(false);
  arm.setAllNowSoftStartUp(alpha_Base, alpha_Shoulder, alpha_Ellbow, alpha_Wrist,WRIST_ROTATION, GRIPPER_POS);
  //This method allows a custom start position to be set, but the setAllNow method MUST be run
  //immediately after the begin method and before any other movement commands are issued.

  //NOTE: The begin method takes approximately 8 seconds to start, due to the time required
  //to initialize the power circuitry.
  
  Serial.println("Initialization Complete");

  digitalWrite(RELAIS_POWER,HIGH); // Relais is switched on -> Powr-Shield has power + arm moves to "custom" positon

}

// 5) START READOUT
void loop() {

// The robot waits on a serial command to get to new position
// TAKE CARE TO JUST SEND RIGHT COMMANDS! THERE IS NOW ADDITIONAL SAFETY/REASONABLENESS CHECK HERE!

  while (Serial.available()) {
    arm.safeDelay(10);            // Delay without interrupting PWM for Servo Drivers

    // Radout of serial line
    if (Serial.available() > 0) {
      char c = Serial.read();
      readString += c;
    }

    update = true;
  }

  /*
Transmitted Char-Array/String:
Angle 1: xxx Base | Angle 2: xxx Schulter | Angle 3: xxx Ellbogen | Angle 4: xxx Wrist

Type: Sign + 3 digits -> 4digits per angle
composition of one command:
x x x x  ,  x x x x  ,  x  x  x  x   ,   x  x  x  x
0 1 2 3  4  5 6 7 8  9  10 11 12 13  14  15 16 17 18
*/


  if (update == true) {
    // Readout individual angles + convert to integer
    digitalWrite(STS_LED,HIGH); // LED on = Moving started
    String Str_alpha_Base = readString.substring(0, 4);
    String Str_alpha_Shoulder = readString.substring(5, 9);
    String Str_alpha_Ellbow = readString.substring(10, 14);
    String Str_alpha_Wrist = readString.substring(15, 19);

    alpha_Base = Str_alpha_Base.toInt();
    alpha_Shoulder = Str_alpha_Shoulder.toInt();
    alpha_Ellbow = Str_alpha_Ellbow.toInt();
    alpha_Wrist = Str_alpha_Wrist.toInt();

    // Move Robot
    setAngles(alpha_Base, alpha_Shoulder, alpha_Ellbow, alpha_Wrist);

    //clear variables
    readString = "";
    update = false;
    digitalWrite(STS_LED,LOW);  // LED off = Moving over
    
    // Delay is okay, because the Matlab Script is waiting for 4sec anyway
    // The Steppers move sometimes arbitory after the set command -> Try to lowpass this moves
    delay(1000); 
    
    // Evaluating Base Angle using extra Sensor + send the measured value via Serial Command    
    alpha_Base_meas = evaluatePoti_Mean();
    alpha_Base_meas_Str = String(alpha_Base_meas,2);
    Serial.println("...Braccio Angle. Base = " + alpha_Base_meas_Str + "| Shoulder = " + Str_alpha_Shoulder + "| Ellbow = " + Str_alpha_Ellbow + "| Wrist = " + Str_alpha_Wrist);

  }
}


// 6) FUNCTIONS

void setAngles(int alpha1, int alpha2, int alpha3, int alpha4) {
  
  // Check, if the angles can be set due to limits of system
  bool update_angles = true;
  if (alpha1 < base_min) {
    update_angles = false;
  }
  if (alpha1 > base_max) {
    update_angles = false;
  }
  if (alpha2 < shoulder_min) {
    update_angles = false;
  }
  if (alpha2 > shoulder_max) {
    update_angles = false;
  }
  if (alpha3 < ellbow_min) {
    update_angles = false;
  }
  if (alpha3 > ellbow_max) {
    update_angles = false;
  }
  if (alpha4 < wrist_min) {
    update_angles = false;
  }
  if (alpha4 > wrist_max) {
    update_angles = false;
  }


  // Set Angles
  if (update_angles == false) {
    Serial.println("...Cancel due to limit");

  } else {

    arm.setAllNowSynchron(alpha1, alpha2, alpha3, alpha4, WRIST_ROTATION, GRIPPER_POS);
  }
}



double evaluatePoti() {
  uout_x_raw = analogRead(PotiPin);
  uout_x = (double)uout_x_raw * (Uref_ADC / 1024.0);

  /*
  // OPTION 1: USING CALIBRATED VALUES
  // is creating more precise results
  */

  alpha_meas = alphaBase_Lin_a1 * uout_x + alphaBase_Lin_a2;
  return alpha_meas;

  /*
  // OPTION 2: USING THE CORRELATION OF THE DESIGN
  // is less precise (because the effective electrical length of the potentiometer is somehow tricky to measure)
  */

  /*
  Ucc = (double)analogRead(UccPin) * (Uref_ADC / 1024.0) * 2;
  k = Ucc / lpoti;
  x = uout_x/k;
  x_s = x0-x;
  alpha_meas_rad = asin(x_s / l);
  alpha_meas = alpha_meas_rad * RAD_TO_DEG;
  return alpha_meas;

  //In case a check is necessairy:
  //Serial.println("uout_x = " + String(uout_x) + "V(Raw=" + String(uout_x_raw) + "), x = " + String(x) + "mm, x_s = " + String(x_s) + "mm, alpha_meas_rad = " + String(alpha_meas_rad) + "rad, alpha_meas = " + String(alpha_meas) + "°");

  */



  
}

double evaluatePoti_Mean(){
  // Readout the Potentiometer & arith average them (Low Pass Filter of Data)

  double alpha_meas_temp =0.0;
  double alpha_meas_sum =0.0;

  int num_avgs = 10; // 10 Averages are selected

  for(int i_avg =0;i_avg<num_avgs;i_avg++){
    alpha_meas_temp = evaluatePoti();
    alpha_meas_sum=alpha_meas_sum+alpha_meas_temp;
    delay(10);
  }

alpha_meas_sum = alpha_meas_sum/((double)num_avgs);

return alpha_meas_sum;
}

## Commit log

2024-12-17 Small Fixes in Comments
    [HallSensor_Halterung_Z-Axis.0006.ipt, HallSensor_Halterung_Z-Axis.0007.ipt, HallSensor_Halterung_Z-Axis.ipt, HallSensor_Holder_Y-Axis.0010.ipt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]
2025-08-28 Updated a lot: * Added 6_Documentation (editable Docs) * Changed Path to original Robot from TinkerCAD (link to their files) * Edited the PartLists and added all mechanical Components * Added an exam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
    [Aruco_Adapter_Basis-BiggerSize.ipt, Aruco_Adapter_Basis-BiggerSize.stl, Aruco_Adapter_Basis.ipt, Aruco_Adapter_Basis.stp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]
